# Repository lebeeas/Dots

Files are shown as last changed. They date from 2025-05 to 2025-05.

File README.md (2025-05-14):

# Dots: Devices for One-handed Tying of Shoelaces

The **Dots**, short for _**Devices for One-handed Tying of Shoelaces**_, are a pair of small, **3D-printed** gadgets you clip onto your shoelaces so you can fasten and unfasten them magnetically, without tying a traditional knot. 

They were created mainly to **help people with limited hand or arm mobility**, seniors who lack finger strength or dexterity, or anyone who finds it hard to bend over long enough to tie shoes (_and anyone looking for a quicker, fuss-free alternative to regular laces_).

untitled4_modif

Until now, the usual go-to has been shoes with **Velcro straps** or, in extreme cases, **asking someone else to help each time** you put your shoes on. The Dots offer an **open-source** solution that works with your existing footwear: everything from sneakers to dress shoes (_there aren’t any convenient, ready-made alternatives on the market for those_).

Each device consists of two main pieces: a “top” half and a “bottom” half that each attach to one lace. When you bring them together, the magnets snap them into place, letting you tighten or loosen your shoes, **even with just one hand**.

SnapGif

## Materials & Dimensions
Both halves were printed in PLA (_polylactic acid_), a plastic material.

**Top half**

- Size: 27.6 × 27.6 × 4.5 mm
- Weight: ~2 g (_excluding magnets, screw, washer and nut_)
- Filament used: ~0.72 m

**Bottom half**

- Size: 27.6 × 27.6 × 4.0 mm
- Weight: ~2 g (_without magnets_)
- Filament used: ~0.65 m

**4 x Magnets**: 8.0 × 3.0 × 2.0 mm

**1 x Screw**: I didn’t understand how screw names work. This is the one I used:
screw
> Not exactly a professional drawing.
> All measurements are in millimeters (mm).

> [!IMPORTANT]
> The important thing is that the screw length equals the assembled device height (8 mm).

**1 x Nut**: Standard Hex Nut M3

**1 x Washer**: Flat, 3.0 mm inner diameter, 7.0 mm outer diameter

untitled7_modif

## Print Settings
- **Supports**: Yes (with the pieces placed so magnet slots face up)
- **Layer** height: 0.2 mm
- **Infill**: 40%, Gyroid pattern

## Design Details
Each piece has a recess that guides the opposite lace into place when **the magnets click together**. The magnets sit visibly in their slots so you can drop them in after printing. This “_industrial_” look ensures compatibility with any printer: high-end or budget models (_like mine_). 
If you want a sleeker finish and can pause your printer mid-job, you could enclose the magnet slots in the model, stop to insert magnets, then resume printing to lock them in. 
_I didn’t…just a bit of glue does the job perfectly :)_
I avoided moving parts to simplify maintenance and maximize lifespan, even though hinges or clips might have looked fancier.

## How to Assemble One Device

AssembleGif

### From the print bed → 
Remove both halves and clean off supports. You’ll find them in two spots: 
- The hex-shaped cavity on the upper half
- the rounded rectangular trough at the edge of each piece

### Put it together →

- The magnets should be inserted into their designated slots. For the first half, there’s **no need to check their orientation**, but for the second half, you’ll need to make sure the two parts, and therefore the magnets, connect via the “flat” side, meaning the side where the magnets aren’t visible.
Also, the two halves must align with the lace holes facing opposite sides. A dab of **glue** keeps them from shifting.
- Place the nut in the hex slot, insert the washer and the screw from the opposite side, and tighten (no need to crank it down hard).
- You should now have these two finished halves:

TurnaroundGif

### Mount on your shoes →

- Slip on the shoe and hold the device with its halves apart.
- Keep the laces threaded as usual but loose.
- Feed each lace end through the entry hole in its half.
- Snap the halves together, then pull the lace ends until the shoe feels snug (just like the first step of tying a knot).
- Tuck any excess lace by either:
  - Tying a small hidden knot near the exit hole and trimming the rest, or
  - Weaving the leftover length through the side eyelets like a stitch for a tidy look.

instructions

> [!WARNING]
> If you fit into one of the target groups, this last step might be tricky or impossible without help. I’m working on it. Sorry.

**Repeat these steps for the other device** that will go on the other shoe.



## A Few Tips
**Don’t overtighten the screw**. The nut simply keeps it from backing out, and once it’s flush with the plastic you’re all set.

Always let **the halves meet on their flat faces** so the magnets aren’t under constant pull, which could weaken their hold over time.

## Future Improvements

Add a small tab on each half to make unfastening easier. Right now you have to grip the side of one piece, which can be tough for some.

Design a covering plate to hide the magnets for a cleaner look.

> [!NOTE]
> I’ve been using this version **daily since March 2025** without issues. I’ll update this write-up each month if the design changes or any problems arise.

## Open Source & License
This project is released under an MIT license.

If you republish this project or a modified version, it would be nice if you credited the original source (this one). Thanks!

All 3D files (.STL), drawings, and instructions are free on this GitHub (no account needed).

legacy
> Previous iterations. Some worked better than others...

If you come across any errors, inaccuracies, or typos, feel free to reach out!
Send me an email at pescettistudio@gmail.com.

-- Riccardo Biasolo

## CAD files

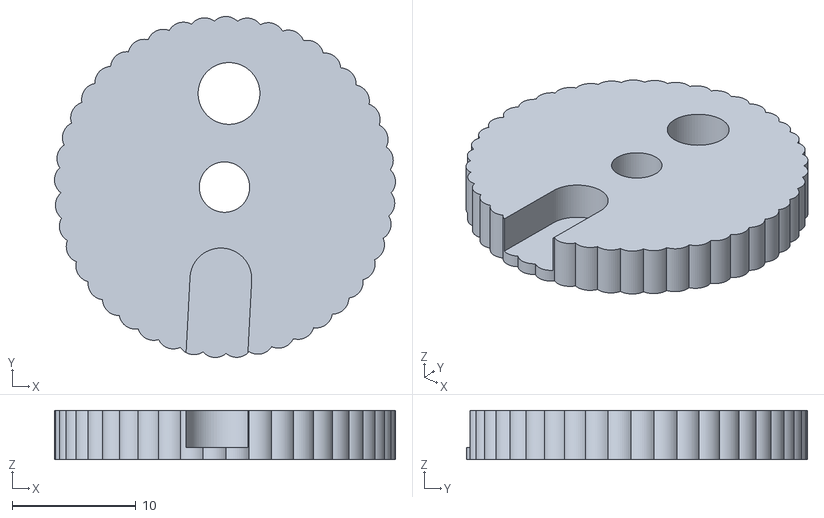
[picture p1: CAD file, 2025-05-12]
LowerPart.stl
27.6 x 27.6 x 4.00

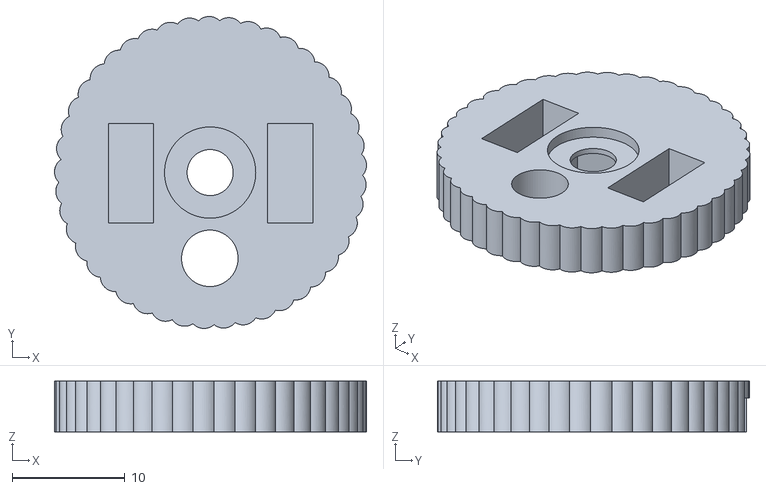
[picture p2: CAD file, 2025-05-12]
UpperPart.stl
27.6 x 27.6 x 4.50
